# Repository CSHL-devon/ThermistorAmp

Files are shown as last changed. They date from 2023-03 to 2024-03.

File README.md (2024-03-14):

# Thermistor Amplifier

A thermistor amplifier for capturing sniff signals in rodents

## General Use

The circuit takes +5V DC and converts to +/-5V DC for the amp. Using the bias trimmer, you can roughly zero the input from the thermistor, allowing +/-5V swings depending on which side of the sniff you're on. I say roughly because the temperature is never static, so the baseline will drift up and down over the experiment. I considered using a chopper amp to pin the baseline to zero, but there's too much signal loss.  

The Gain trimmer will adjust the level of amplification. The range is not huge, but some thermistor implantations run hotter than others, so it's nice to have a bit of flexibility.

The thermistor gets connected to the 3-position screw terminal. "+5V" is going out from the board into the thermistor, while "In" is the input from the thermistor to the amp. The third position is connected to ground so you can connect cable shielding, which is techinally optional, but very highly recommended.

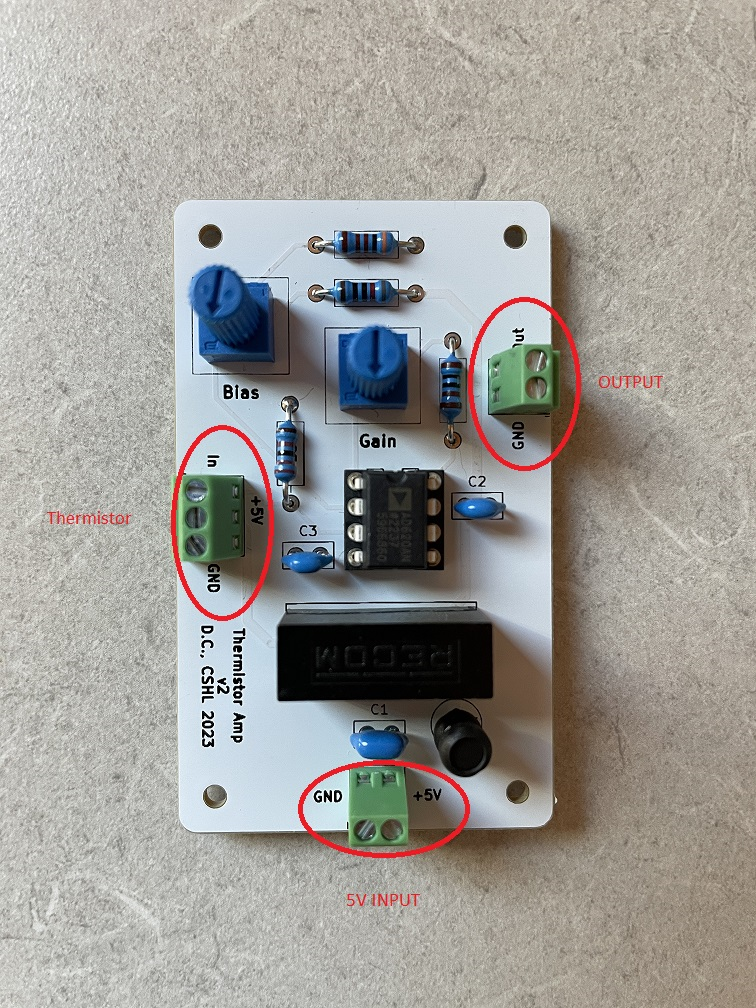
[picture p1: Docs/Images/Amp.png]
  

## Building

UPDATE: By popular demand, this is now made exclusively with through-hole parts, so building is trivial.

### Build Order

- Resistors
- IC Socket
- Capacitors
- Inductor
- Screw Terminals
- DCDC Converter
- Trimmers

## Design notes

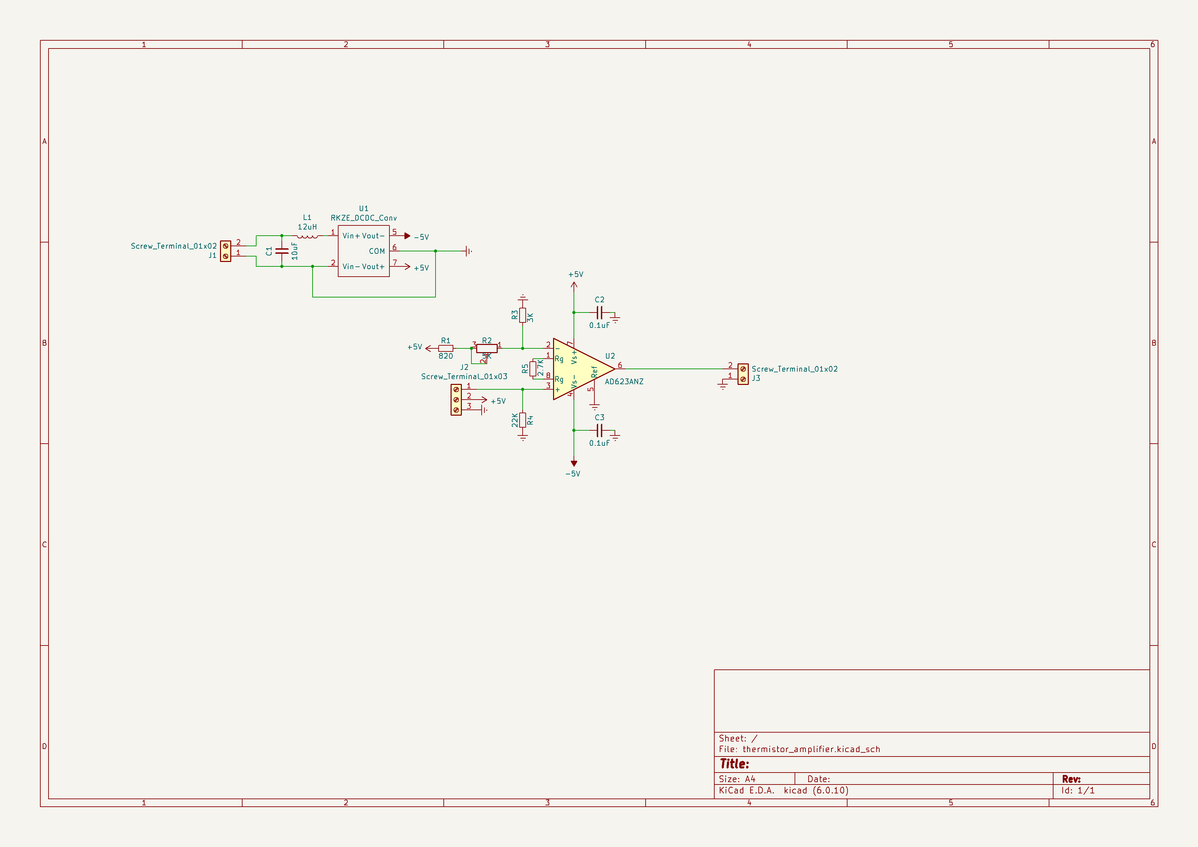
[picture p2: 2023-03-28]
Docs/Images/ThermAmp_Schematic.png

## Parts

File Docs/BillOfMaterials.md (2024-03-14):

## Bill of Materials

1x  Custom PCB (see zipped gerber file in KiCAD directory)  
1x  +/-5V DCDC Converter (Digi-Key# 945-3174-ND)  
1x  12uH Inductor (Mouser# 652-RLB0608-120KL) - Digi-Key doesn't stock this, but its too cute and tiny not to use  
1x  10uF Ceramic Capacitor (Digi-Key# 445-181080-ND)  
2x  0.1uF Ceramic Capacitor (1206) (Digi-Key# 445-175524-ND)  
1x  1K Ohm Resistor (1/4W) (Digi-Key# 1.00KXBK-ND)  
1x  820 Ohm Resitor (1/4W) (Digi-Key# 13-RT1206FRE07820RLCT-ND)  
1x  5K Ohm Trimmer (Digi-Key# MFR-25FBF52-820R-ND)  
1x  3K Ohm Resistor (1/4W) (Digi-Key# 3.01KXBK-ND)  
1x  2.7K Ohm Resistor (1/4W) (Digi-Key# P2.7KBCCT-ND)  
1x  22K Ohm Resistor (1/4W) (Digi-Key# MFR-25FBF52-22K-ND)  
1x  8P IC Socket (Optional) (Digi-Key# ED58083-ND)  
1x  Instrument Amp (Digi-Key# 505-AD620ANZ-ND)  
2x  2P Screw Terminal (Digi-Key# 277-1273-ND)  
1x  3P Screw Terminal (Digi-Key# 277-1274-ND)  
4x  M2x5mm Screws  

1x  Thermistor (per animal) (Digi-Key# 223-1558-ND)
- These have gotten very expensive. We're testing alternatives and will update this BoM if we find a suitable replacement

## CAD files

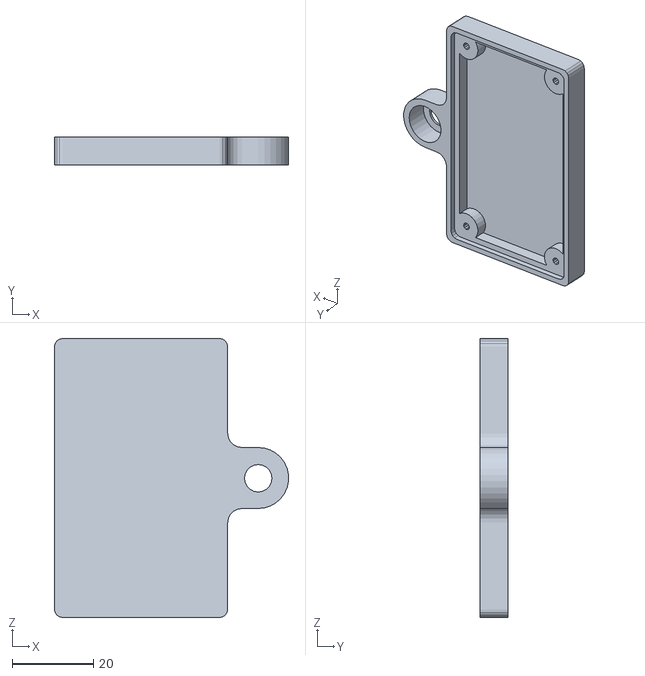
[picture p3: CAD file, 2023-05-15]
CAD/Thermister_Amp_Mount.stl
57.6 x 7.00 x 68.6

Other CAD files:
CAD/OldVersions/Thermister_Amp_Mount.0005.ipt
CAD/Thermister_Amp_Mount.ipt

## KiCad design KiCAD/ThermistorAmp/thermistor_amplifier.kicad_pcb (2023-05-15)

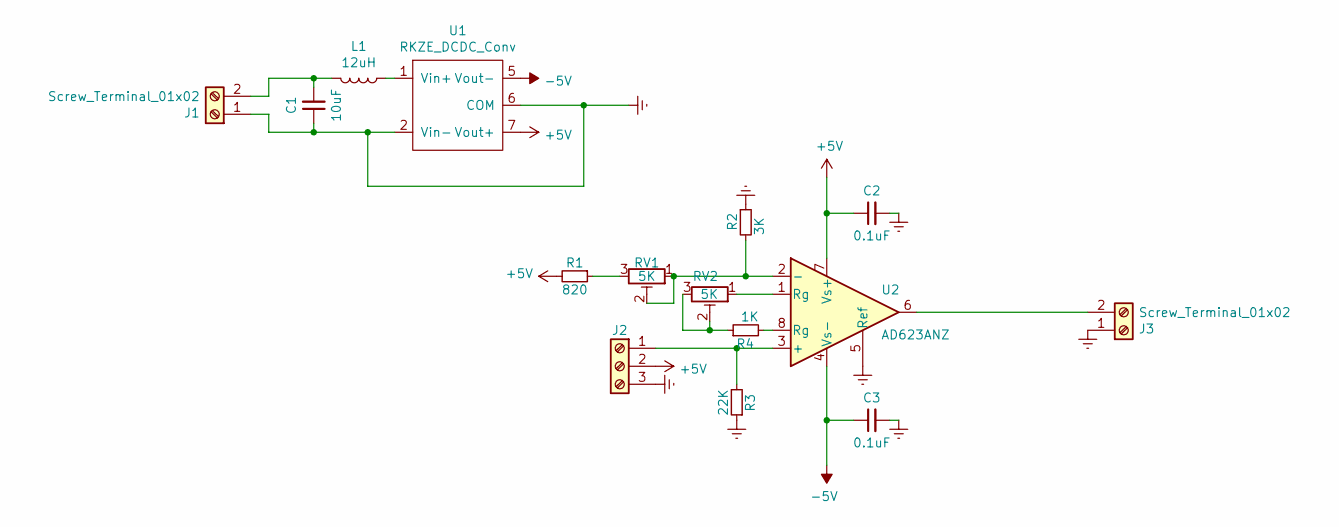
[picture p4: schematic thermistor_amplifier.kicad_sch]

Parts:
C1: 10uF; C_Disc_D5.0mm_W2.5mm_P2.50mm
C2, C3: 0.1uF; C_Disc_D5.0mm_W2.5mm_P2.50mm
J1, J3: Screw_Terminal_01x02; TerminalBlock_Phoenix_MPT-0,5-2-2.54_1x02_P2.54mm_Horizontal
J2: Screw_Terminal_01x03; TerminalBlock_Phoenix_MPT-0,5-3-2.54_1x03_P2.54mm_Horizontal
L1: 12uH; C_Radial_D5.0mm_H7.0mm_P2.00mm
R1: 820; R_Axial_DIN0207_L6.3mm_D2.5mm_P10.16mm_Horizontal
R2: 3K; R_Axial_DIN0207_L6.3mm_D2.5mm_P10.16mm_Horizontal
R3: 22K; R_Axial_DIN0207_L6.3mm_D2.5mm_P10.16mm_Horizontal
R4: 1K; R_Axial_DIN0207_L6.3mm_D2.5mm_P10.16mm_Horizontal
RV1, RV2: 5K; Potentiometer_Bourns_3386P_Vertical
U1: RKZE_DCDC_Conv
U2: AD623ANZ; DIP-8_W7.62mm

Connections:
+5V: C2.1, J2.2, R1.2, U1.7 (Vout+), U2.7 (Vs+)
-5V: C3.1, U1.5 (Vout-), U2.4 (Vs-)
Earth: C1.1, C2.2, C3.2, J1.1, J2.3, J3.1, R2.1, R3.1, U1.2 (Vin-), U1.6 (COM), U2.5 (Ref)
unnamed: C1.2, J1.2, L1.2
unnamed: J2.1, R3.2, U2.3 (+)
unnamed: J3.2, U2.6
unnamed: L1.1, U1.1 (Vin+)
unnamed: R1.1, RV1.3
unnamed: R2.2, RV1.1, RV1.2, U2.2 (-)
unnamed: R4.1, RV2.2, RV2.3
unnamed: R4.2, U2.8 (Rg)
unnamed: RV2.1, U2.1 (Rg)

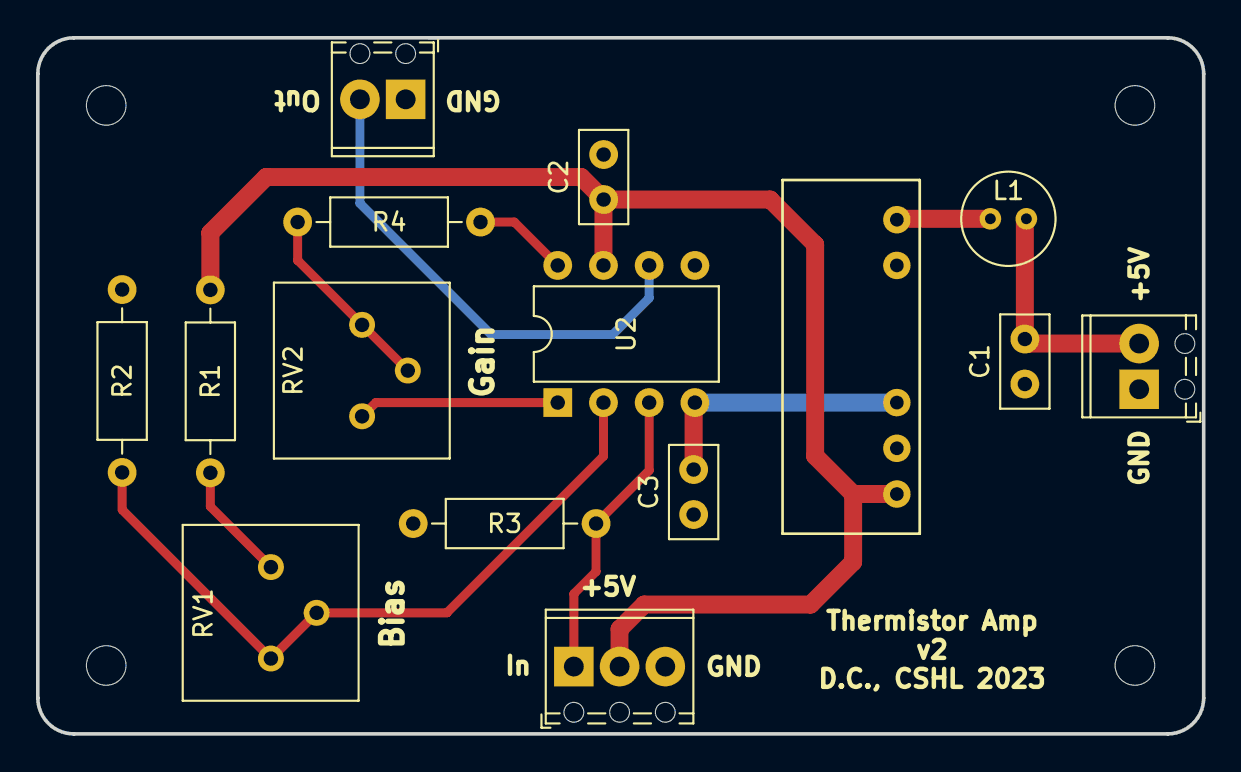
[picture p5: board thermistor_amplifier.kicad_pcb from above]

Board: 2 copper layers, 64.8 x 38.7 mm, 15 parts (0 on the bottom side), 12 nets.
